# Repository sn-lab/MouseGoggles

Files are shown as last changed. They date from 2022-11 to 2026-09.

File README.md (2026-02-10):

**MouseGoggles**: A dual-SPI-display mouse-sized VR headset for mouse neuroscience and behavior research, powered by Raspberry Pi and the Godot game engine. Check out the paper at Nature Methods! https://www.nature.com/articles/s41592-024-02540-y

(left) A Raspberry Pi 4 uniquely controlling 2 circular displays. (right) Render of a head-fixed mouse on a treadmill with a VR headset

- Find a bug, have a suggestion, or want to make a feature request? Submit an [issue](https://github.com/sn-lab/MouseGoggles/issues) or start a [discussion](https://github.com/sn-lab/MouseGoggles/discussions)!

**Work in progess**

* Updating and improving [MouseGoggles EyeTrack 2.0](https://github.com/sn-lab/MouseGoggles/tree/main/Versions/EyeTrack/2.0) eye imaging quality and software improvements.

**Previous Updates**

* (Jan 2026) Added intial files for [MouseGoggles EyeTrack 2.0](https://github.com/sn-lab/MouseGoggles/tree/main/Versions/EyeTrack/2.0)! The design is now built around a single Raspberry Pi 5, aiming toward improving eye-tracking quality and a simpler assembly process (though eye-imaging quality is still being worked on).
  
* (May 2025) Big software updates to EyeTrack 1.1, including the first Godot project (2.1) which enables controlling and viewing the eye-tracking cameras from within the game engine! TCP/UDP communication between the Pis enable TTL outputs and eye-tracking videos to be controlled directly from VR experiment scripts.

* (Mar 2024) Added the [MouseGoggles EyeTrack](https://github.com/sn-lab/MouseGoggles/tree/main/Versions/EyeTrack/1.0) headset, for binocular eye/pupil tracking cameras integrated into the headset

# Building a MouseGoggles System

All versions of MouseGoggles were designed using as many readily available, off-the-shelf parts as possible, with only a minimal number of custom parts required to make assembly as simple as possible. To build a MouseGoggles system, navigate to the folder of the version you'd like to build in the [Versions](https://github.com/sn-lab/MouseGoggles/tree/main/Versions) folder and follow the included README for a comprehensive parts list, assembly guide, and software installation instructions. Since some parts included in earlier versions of the system have since been discontinued by the manufacturers, [Eyetrack version 2.0](https://github.com/sn-lab/MouseGoggles/tree/main/Versions/EyeTrack/2.0) is what we recommend building for all use-cases. Version 2.0 is built on an entirely new display platform (Raspberry Pi 5; mipi-dbi-spi) that future versions will be developed from. 

# About MouseGoggles

### The Raspberry Pi and Godot game engine

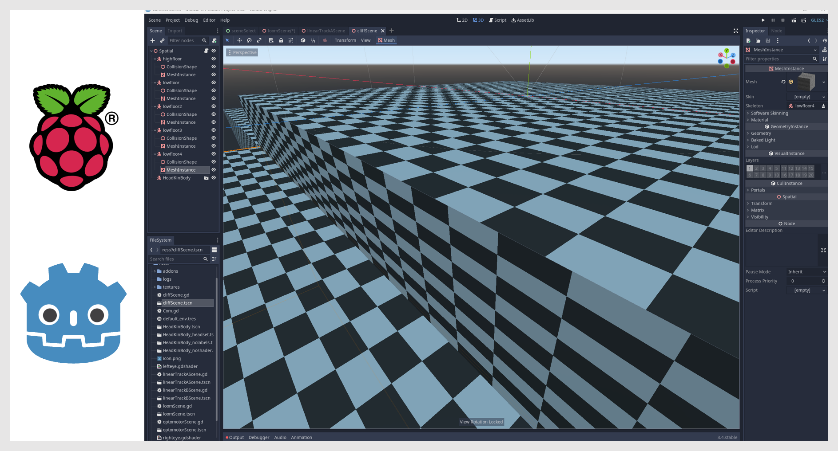
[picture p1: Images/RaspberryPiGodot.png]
Godot game engine running on a Raspberry Pi 4


The heart of the MouseGoggles system is a [Raspberry Pi 4](https://www.raspberrypi.com/products/raspberry-pi-4-model-b/) running the [Godot](https://godotengine.org/) video game engine. Since the displays are relatively low resolution (240x240), an inexpensive single-board computer like a Raspberry Pi 4 is all that's needed to effectively render visual scenes at high (>=60 fps) framerates. The multiplatform game engine Godot makes it easy to create virtual scenes and develop experimental protocols. Examples included in this repo are experiments for visual cliff avoidance, reactions to looming stimuli of various size/velocity ratios, and the syndirectional rotational optomotor response to gratings of various spatial wavelengths. The views rendered for each display are controlled by separate in-game cameras which can be tied together to match the inter-eye distance and angle of a typical mouse. Custom display shaders warp the view from each camera to match the spherical distortion of the Fresnel lenses, intended to create a realistic and immersive experience for the mouse.

### The display driver

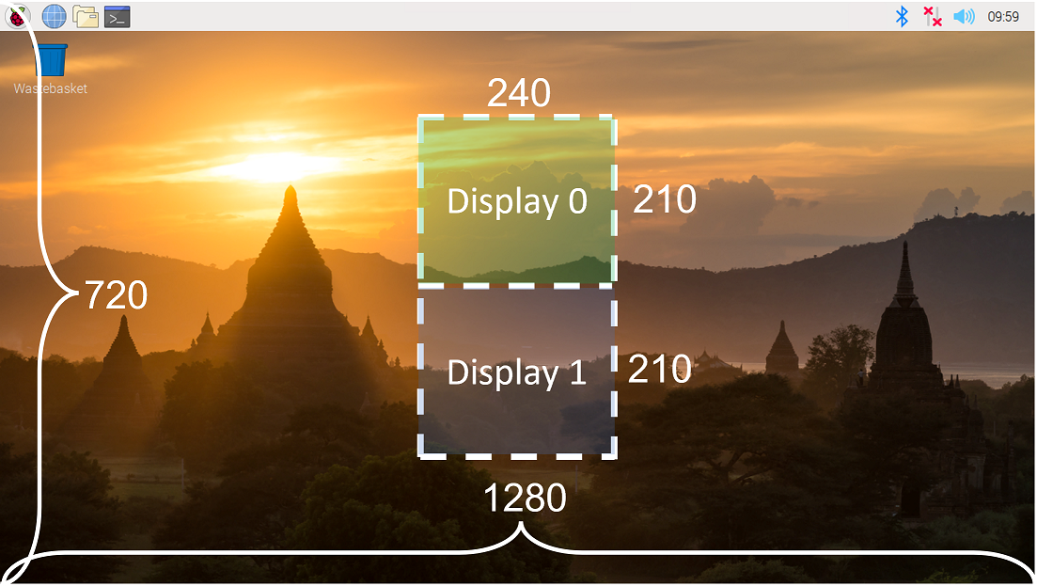
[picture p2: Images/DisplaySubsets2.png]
dual-SPI-display driver streams different frame subsets to two displays


Based on a ["blazing fast" display driver](https://github.com/juj/fbcp-ili9341) for SPI-based displays, the driver included in this repository works by copying the HDMI framebuffer and streaming the image data to the connected displays connected on the Raspberry Pi's SPI port. This means that the headset displays are not limited to displaying what is rendered by Godot; in fact, whatever is displayed on the central 240x420 (WxH) pixel region of the screen is going to be streamed to the displays. If you want to create images or video with some other program, you just have to position it in the center of the display for it to be sent to the displays -- the top 240x210 sent to display 0 (on SPI0 chip-select 0) and the bottom 240x210 to display 1 (on SPI0 chip-select 1).

### The MouseGoggles 1.0 headset

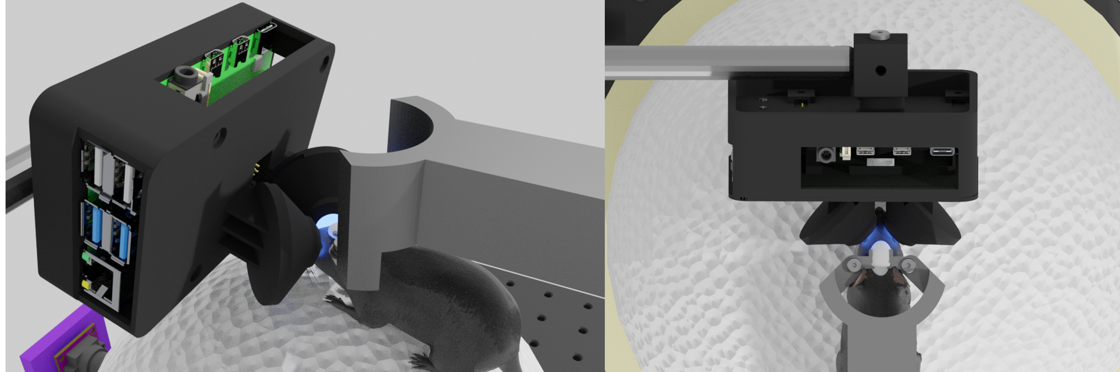
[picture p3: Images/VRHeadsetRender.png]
Render of a fully assembled MouseGoggles headset positioned for a head-fixed mouse


To create an immersive, wide field-of-view (FOV) VR headset from the dual-display Raspberry Pi, a 3D-printed headset case angles the displays inwards and sets them behind Fresnel lenses. These lenses serve two functions: to allow the displays to be positioned very close (<15 mm) to the mouse's eyes while still maintaining a comfortable infinity focal distance, and to spherically distort the displays to cover a wide FOV around each eye. Viewing angles from 0-70 degrees (0-52.5 degrees on the chipped side of the circular display) are linearly mapped onto the 240x210 circular display, resulting in an angular resolution of ~0.64 deg/pixel. With the 2 displays angled 45 degrees inward from straight ahead, the binocular headset covers a wide FOV: 140 degrees vertical and 230 degrees horizontal, with ~25 degrees of binocular overlap. Even greater horizontal FOVs are possible with greater display angles. This headset is the first official version of MouseGoggles (1.0), but newer versions have been developed which add new functionality, such as a smaller form-factor headset detached from the Raspberry Pi (1.1-1.2, 1.5), adjustable inter-eye distance (1.2-1.5), and an easier to assemble design (1.5). For more details on each MouseGoggles version, see the [Versions](https://github.com/sn-lab/MouseGoggles/tree/main/Versions) folder.

### MouseGoggles Mono 1.0

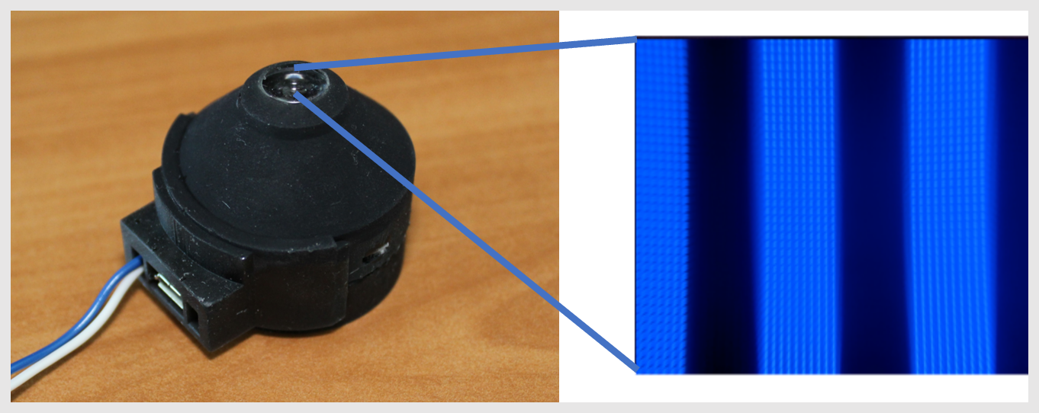
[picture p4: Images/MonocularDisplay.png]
Monocular display for basic visual stimuli (e.g. drifting gratings)


In addition to the binocular MouseGoggles system, a monocular eyepiece version can be built using a single display, lens, and microcontroller. Where the headset is ideal for complex virtual reality experiments and behavioral research, the monocular display is ideal for simple visual stimulation for basic visual neuroscience applications. The fast microcontroller [Teensy4.0](https://www.pjrc.com/store/teensy40.html) and [Adafruit graphics library](https://learn.adafruit.com/adafruit-gfx-graphics-library/overview) is used to display simple shapes and moving patterns such as drifting gratings and flickers. For more details, see [Versions/Mono/1.0]().

### Treadmills

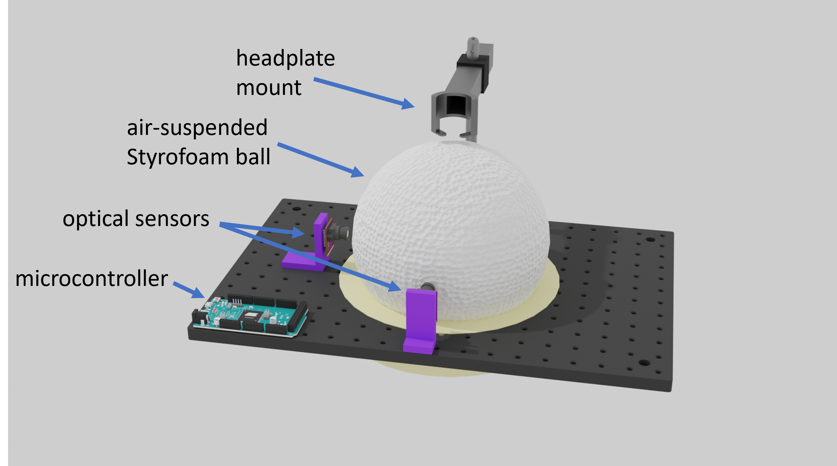
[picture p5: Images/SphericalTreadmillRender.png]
Render of a spherical treadmill system with a head mount, air-suspended Styrofoam ball, motion sensors, and microcontroller


The MouseGoggles VR headset was developed and tested using a two different treadmills for simulated walking: the spherical treadmill setup as described [here](https://pubmed.ncbi.nlm.nih.gov/19829374/) and the linear treadmill described [here](https://github.com/janelia-experimental-technology/Rodent-Belt-Treadmill/tree/main). These treadmills use sensors to detect treadmill motion and a microcontroller to transmit this movement information to external devices. By modifying the microcontroller code, we can adapt these systems to send treadmill motion to the Raspberry Pi over USB through computer mouse emulation. Forward movement (i.e. "pitch" of the spherical treadmill, or any movement of the linear treadmill) is mapped as mouse y movement, turning (i.e. "yaw" of the spherical treadmill) is mapped as x movement, and sideways motion (i.e. "roll" of the spherical treadmill) is mapped as mouse scroll wheel movement. The Godot game engine converts these detected mouse movement events into the corresponding camera movements in the virtual scene. This setup allows the human user to test the game environments and experiments using a standard computer mouse or touchpad, and to use this VR system with any type of treadmill control system that can be translated through the standard USB mouse communication protocol. To set up one of these treadmill systems with MouseGoggles (including adding a headbar and mount to head-fix a mouse above the treadmill), see the [README](https://github.com/sn-lab/MouseGoggles/blob/main/Other%20Hardware/Installation%20README.md) in the [Other Hardware](https://github.com/sn-lab/MouseGoggles/tree/main/Other%20Hardware) folder.

# Published Data

Multiple datasets have been collected for validating and testing different aspects of the MouseGoggles system for neuroscience applications, including 2-photon imaging for visual stimulation, hippocampal electrophysiology for place cell activity during virtual navigation, and video recordings of mouse behaviors during looming stimulus presentation. Check out our [preprint on Research Square](https://doi.org/10.21203/rs.3.rs-3301474/v1) for explanation and visualization of these datasets. Data, metadata, and code to process and analyze these datasets are included in the [Published Data](https://github.com/sn-lab/MouseGoggles/tree/main/Published%20Data) folder of this repository; large raw data files unsuitable for github are hosted on [Figshare](https://figshare.com/articles/dataset/Raw_image_files/24039021). 
To reproduce the published results from each of these datasets, follow the instructions in the [Description of Contents](https://github.com/sn-lab/MouseGoggles/blob/main/Published%20Data/Description%20of%20Contents.md) file, noting the software dependencies listed here:

```
* Matlab 2022b
* Python 2.8.8
* suite2p (suite2p.org)
* https://github.com/misaacson01/NoRMCorre
* https://github.com/lolaBerkowitz/SNLab_ephys
* https://github.com/nelpy/nelpy
* https://github.com/ryanharvey1/neuro_py
* https://github.com/ryanharvey1/ripple_heterogeneity
```

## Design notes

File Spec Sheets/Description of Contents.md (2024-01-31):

# Description of Contents

This folder contains specification sheets for the circular displays used in the various MouseGoggles versions. For spec sheets on the assembled display and display drivers for MouseGoggles versions 1.0-1.3, consult the files for the "1.08inch display". To more quikly refer to the pinouts of these circular displays and their connectors on MouseGoggles pcbs, refer to the pinouts.ppt file. For spec sheets relevant to the display used MouseGoggles version 1.5, consult the files for "waveshare display".

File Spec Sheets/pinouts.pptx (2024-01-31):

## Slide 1

Raspberry Pi pinouts used (for MouseGoggles)

2 | 4 | 6 GND | 8 | 10 | 12 | 14 | 16 | 18 | 20 | 22 | 24 CE0 | 26 CE1 | 28 | 30 | 32 | 34 | 36 | 38 | 40
1 3V | 3 | 5 | 7 | 9 GND | 11 | 13 | 15 reset | 17 | 19 MOSI | 21 MISO | 23 SCLK | 25 GND | 27 | 29 fmark | 31 dc | 33 | 35 | 37 | 39

Teensy 4.0 pinouts used (for MouseGoggles Mono)

| | | | | | | | | | | | reset | SCLK

GND
3V

| | | | | | fmrk | DC | | | | CE0 | MOSI

13-pin FPC connector pinouts (for 1.08” displays)

1 3V | 15 reset | 23 SCLK | 19 MOSI | 25 GND | 25 GND

25 GND | 1 3V | 24 CE0 | 31 dc | 29 FMARK | 1 3V | 25 GND

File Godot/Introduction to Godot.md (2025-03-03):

# About Godot

Godot is a free, open-source, 2D and 3D game engine popular with indie game developers, though in the context of the MouseGoggles VR system, it is a flexible experiment design platform that is powerful enough to generate complex 3D environments, yet lightweight enough to run on a Raspberry Pi 4. It can be used to generate simple 2D images, video, and animations for visual neuroscience applications, or more commonly, it can generate 3D virtual environments and conduct complex behavioral neuroscience experiments. 

Godot is multi-platform engine, meaning it can run on a PC, mac, or Linux computer. And a Godot project does not need to be compiled; this means that if you want to create or edit a Godot project on one computer, you can simply copy the project folder and run it on any other computer (even one using a different operating system) without re-compiling it there.

The [official online documentation](https://docs.godotengine.org/en/3.0/) makes it [relatively] easy to get started from scratch, and there are many excellent [tutorials](https://docs.godotengine.org/en/stable/community/tutorials.html) to help you get started. This short guide is not meant to completely replace those tutorials or make you a Godot expert, but to familiarize you with the Godot engine to the point that you're able to run VR experiments with MouseGoggles and to make simple edits and customizations of the experiments for your own purposes.

### Installing and running the Godot game engine

On a Windows or Mac PC, download the Godot Engine from [godotengine.org](godotengine.org). To use the same software version that is used on the Raspberry Pi 4, download [version 3.2](https://godotengine.org/download/archive/3.2-stable/).  

On a Raspberry Pi 4, Godot can be installed by opening the command terminal and entering each line, one at a time:

```
sudo apt update
sudo apt install flatpak
flatpak remote-add --if-not-exists flathub https://flathub.org/repo/flathub.flatpakrepo
flatpak install flathub org.godotengine.Godot
```

After installation is complete, Godot can be run on a Raspberry Pi with the following command line:

```
flatpak run org.godotengine.Godot
```

### Project manager: importing and running projects

In the context of the MouseGoggles VR system, a project can be thought of as a collection of experiments the can be edited and run on the Raspberry Pi. When Godot is first run, a project manager window will open and list all Godot projects available on your computer. If you've downloaded a project folder from elsewhere (e.g. from a Github repository, or from another computer), this project will need to be imported by Godot before it can be edited or run. 

To import a project, start the Godot program to be brought to Godot's project manager. Click the `import` button on the right, and navigate into your new project folder. Locate the `project.godot` file inside that folder and select it to import the project. After being imported, the project can be run directly, or it can be opened into the Godot Editor where all of the project's experiment files can be read and modified. The project can also be run from inside the editor by clicking the small green arrow on the top-right side of the window.

### Editor

In the Godot Editor window, there are mutliple menus and panels that give you access to view and edit different aspects of the project. Across the top are the main menus where overall project settings and defaults can be customized (e.g. Scene, Project, Debug, and Editor), followed by the workspace tabs where different project files can be viewed and modified (e.g. 2D scene, 3D scene, and script files). Along the left and right sides of the window are the panels (e.g. Scene, Filesystem, and Inspector) which offer more granular views of specific files, scenes, and nodes in the project. And in the center of the window is the main workspace, where the currently selected file (scene or script) can be visualized. 

##### Scenes, Nodes, and Scripts

Building a game or experiment with the Godot editor is primarily accomplished using scene and script files. The "scene" file (denoted by the `.tscn` file extension) defines the contents and layout of a virtual environment, and the script file (denoted by the `.gd` file extension) contains instructions for how the scene functions, or how a user (human or mouse) interacts with the scene. 

A scene is built from a series of nodes, which can be thought of as environmental building blocks that give new characteristics to the scene. Nodes are hierarchical: they can be "children" of the scene, where new objects or surfaces (for example) can be defined, or they can be children of other nodes, giving additional characteristics (e.g material or physical properties) to its parent node. In MouseGoggles Godot projects, nodes are often used to build objects or surfaces in the 3D scene; for example, the `MeshInstance` node can create a surfaces for the objects, floors, or walls of a 3D environment.

After the 3D layout has been defined by a scene file, a script file (or files) can be attached to the scene to control the behavior of the scene and define events that take place in that scene. Godot scripts use the object-oriented programming paradigm, not unlike C++ or Python, so some programming knowledge is required to perform significant edits to the experiment or to create new experiments (Godot recommends this free, online Intro to Computer Science course [CS50x 2024](https://cs50.harvard.edu/x/2024/) as a general programming tutorial). Scripts can be attached to any node of a scene, where the script will control the behavior of that node. In MouseGoggles Godot projects, scripts are typically attached to the root (i.e. parent)`spatial` node of a 3D scene, which then defines the logical flow of an experiment using that scene. Script files tend to be structured with a familiar programming layout, beginning with defined variables at the top, followed by a setup function that runs once at the beginning of the experiment (`func _ready():`), a loop function that runs for every rendered frame of the experiment (`func _process(delta):`), and finished with any additional functions that may be called by the script. Properties of a scene (e.g., the [x,y,z] location of a virtual object located the scene) can be assigned to variables at the top of the script and then modified during the script's functions, thereby granting the script the power to control the properties of the scene and define an experiment.

### Experiment log files

The example Godot experiments for MouseGoggles use a common format for logging experimental data. This format consists of logging the state of a number of variables for every frame. That is, each time the game loop executes, the state of those variables is logged. At the end of each experimental trial, a section of this code will save these variables in a .csv file, in the `logs` folder inside the Godot project folder. 

Each column of data in the csv file represents the values of a single variable; the header at the top of the file shows the descriptive name of these variables. Each row of the csv file shows the value of these variables for each frame.

Different experiments are designed to store different variables that are important for that experiment. For example, in experiments featuring 2D navigation, the mouse's position (x,z) and it's current orientation are important to log, whereas in experiments with only 1D navigation, only the mouse's z position needs to be logged.

### Calibrating an existing experiment

At the top of each experiment script (e.g. `linearTrackScene.gd` in Godot project 1.6), variables are set which descibe many of the experiment's parameters. Some of these parameters may need to be changed depending on your specific experimental setup. Beginning in Godot project 2.0, many of these parameters which are common across all experiments (e.g. parameters about the headset configuration) are instead contained in the `commonSettings.gd` script to remove redundancy. Listed below is a few parameters which are mostly likely to change, though for each experiment you run, it is wise to first look through all of the parameters to verify they make sense for your experiment.

* `trial_duration`: The duration (in s) of each trial, before a timeout is reached and the next trial starts.

* `num_reps`: The number of trial repetitions before the experiment is finished.

* `eye_pitch`: The pitch angle (in degrees) of the headset, relative to the horizon.

* `head_roll`: The roll angle (in degrees) of the headset, relative to the horizon.

* `mouse_gain`: The movement sensitivity of input signals: higher values will increase the speed virtual movement.

### Creating a new experiment

If you want to design new experiments of your own, you may choose to follow the tutorials listed at the top to create a new exxperiment from scratch. Alternatively, a simpler, faster way to create an experiment is to select an existing experiment that most closely matches the experiment you'd like to create, and copy/customize that experiment. The following instructions provide general guidance on creating a new experiment this way by copying and editing an existing project.

1. Copy the existing project, and give it a new name
   
   * Copy the "MouseVR Godot Project X.X" folder that you wish to adapt, and give the copy a unique name
   
   * Open Godot, and in the project manager window, import the new project folder you just created. The project will still have the original project name, so rename it to match the new folder you just created (In the editor window: Project>Project Settings>Config>Name)

2. Run the new project, copy an existing experiment, and give it a new name
   
   * From the project manager, edit the new project you just created
   
   * Selecting the experiment you wish to modify, copy both the .tscn and .gd files of that experiment. Rename these copied files to describe your new experiment.
     
     (e.g. `new_exp.tscn`; `new_exp.gd`)
   
   * Open up the .tscn file of your new experiment, and view it in the `3D` tab. In the Scene tab, identify the `spatial` node that has an attached script. This will still be the original script that you copied from, so right click the node to detach this script. Right click the node again to attach the new script you just created.

3. Edit the new experiment
   
   * Open the new .tscn file you created and view it in the `3D` tab. Edit the nodes and properties to adapt the scene to fit your desired experiment
   
   * Open the new .gd script you created and view it in the `script` tab. Modify the code to fit your desired experiment.

4. Add the new experiment to the "scene select"
   
   * Open up the sceneSelect.tscn file, and view it in the `2D` tab
   
   * In the Scene window, copy the last MarginContainer node (e.g. "MarginContainer9") and paste it in the empty space below. This will create a new margincontainer and child button node. Rename the MarginContainer node (e.g. "MarginContainer10") and drag it so that it is a child of the VBoxContainer node. This will move your new button to the top of the list of scene buttons. Since this new button will still have the same name as the button you copied, click on the new button, and in the Inspector window, rename the text to match your new experiment.
   
   * Open up the sceneSelect.gd file and view it in the `script` tab.
   
   * Copy a scene variable and rename it to match your new MarginContainer# and new experiment name 
     
     (e.g. `onready var  new_exp_button = get_node("HBoxContainer/VBoxContainer/MarginContainer10/Button")`)
   
   * in the `_ready():` function, copy a line and rename it to match your new scene variable and create a new experiment callback function.
     
     (e.g. `new_exp_button.connect("pressed",self,"_load_new_exp")`)
   
   * Copy a callback function and rename it to the function name you just created, and set it to load your new experiment.
   
   * (e.g. `func _load_new_exp():
     
         get_tree().change_scene("res://new_exp.tscn")`)

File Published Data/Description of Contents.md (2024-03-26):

# Description of Contents

This folder contains datasets and code used in the intial MouseGoggles publication. Raw data, pre-processed data, and analyzed data is included in the "data" folder when possible; large raw data files unsuitable for github are hosted by [FigShare](https://figshare.com/articles/dataset/Raw_image_files/24039021).
For each dataset, Matlab and/or python code used to process and plot data are included. The sections below detail the contents of each dataset folder and how the publication data can be reproduced.

### 2P Imaging

This folder contains two-photon imaging data, experimental protocol metadata, and processing/plotting code for 3 mouse imaging sessions. Raw Imaging data files too large for github are hosted by Figshare at the link above. Also on Figshare are the motion corrected calcium imaging data files associated with these raw data files, located here: https://figshare.com/account/items/24039042
To reproduce the published results from preprocessed data files included in this folder, open the `monoDisplay_VR2_analysis.m` file in Matlab and run section 3. 
Alternatively, To reproduce the data from raw imaging files, download the files from figshare and put each of the 3 raw imaging files into the associated mouse folder (e.g., "rfm0d0t0_mouse1.tif" into the "mouse1" folder). Next open the `monoDisplay_VR2_analysis.m` file in Matlab and run sections 1 and 2 for each mouse folder individually to preprocess these raw imaging files. Section 1 extracts the TTL synchronization signal from the imaging data (indices of the imaging frames at the start of every experimental stimulus set will be contained in the `starts.mat` file) and creates motion-corrected calcium image files. Following the instructions in section 2, these calcium imaging files must next be loaded into suite2p for automatic ROI segmentation and neuron activity extraction, which will generate a "suite2p" folder of data for each imaging file. All neuron activity data needed for analysis and plotting will be contained in`>suite2p>plane0>Fall.mat`. After this has been performed for each mouse dataset, section 3 of `monoDisplay_VR2_analysis.m` can be run to analyze and plot the data. Note however the example neuron plots in section 3 may not work well if the suite2p dataset has changed; if that is the case, new example neurons should be found through manual inspection of the data.
For more details about experimental protocol or to reproduce the experiment yourself, `monoDisplay_VR2_presentation.m` is the monocular display control script which generated and presented the stimulus sets used in this dataset.

### Looming

This folder contains behavioral scoring details and data from 2 independent semi-blind scorers to find mouse startle reactions to looming visual stimuli. In the "Reaction Log" .xlsx files, scorers were given instructions as to how to score video clips of mice reacting to looming stimuli from either a projector VR system or the MouseGoggles VR system. These video clips are stored on Figshare at the link above, in the "loom_videos.zip" file. To reproduce the published results from this dataset, run the `analyze_manual_loom.m` script in Matlab.

### Linear track

This folder contains all logged data from the 5-day continuous loop linear track place learning protocol, performed with 10 mice over 2 datasets. Each dataset contains logged data for 40 track traversals each day over 5 days, from 5 mice. Due to some occasional Raspberry Pi/Godot glitches, some experiments had to be restarted resulting in >40 traversals for some mice on some days; these extra traversals are unused in this analysis. In all logged data files, data is stored in csv format, where each line stored data for a single frame of the game loop, and the columns each store a unique datatype according to the following structure:
column 1: spherical treadmill yaw motion
column 2: spherical treadmill pitch motion
column 3: spherical treadmill roll motion
column 4: mouse x (horizontal) position (locked at 0.5 in this experiment)
column 5: mouse z (position along track) position
column 6: mouse head angle (locked at 180 degrees in this experiment)
column 7: water reward given signal
column 8: lick sensor detection signal
column 9: timestamp (in ms, from program start)
To reproduce the published results from this data, run the `analyze_godot_lineartrackV5B_allsets.m` script in Matlab. To reproduce or visualize this experiment, open the Godot program and select the 'linear track' scene, defined by the game program file `linearTrackScene.gd` in the Godot project folder.

### CA1 Ephys

This folder contains code for processing and plotting electrophysiological recording during continuous loop linear track traversal. The data used by this code is stored according to [CellExplorer data format standards](https://cellexplorer.org/datastructure/data-structure-and-format/) and hosted by Figshare at the link above.
To reproduce the published results from this dataset, download the VR_ephys_8sessions.zip file and unzip it into the CA1 Ephys folder. To plot the processed data, the `plot_vr_place_cells.ipynb` notebook calls the main processing script located in `vr_place_cells.py`. For Windows 10 users, the full environment to run this notebook/script can be installed by creating a conda environment using the environment.yml.

### Eye Tracking

This folder contains code and data for processing and plotting eye/pupil tracking during looming visual stimuli presented to head-fixed mice walking on a linear treadmill. Most raw and processed data are located in this folder, while larger eye tracking and gameplay videos are hosted by Figshare at the link above.

To only reproduce data plots from processed tabular data, this folder contains all the necessary data and code. To fully reproduce the results from this dataset from raw videos, the "MouseGoggles EyeTrack Videos" .zip file will needed to be downloaded from figshare and copied into their matching folders in this repository. 

To reproduce the eye tracking camera calibration, run the `camera_calibration.m` Matlab script loacted in the Camera calibration folder. To preprocess and extract eye data from deeplabcut-labelled eye tracking videos and logged data files, run the `Preprocess_EyeTrack_Loom.m` Matlab script. To generate plots from preprocessed tabular data files, run the raw `Analyze_EyeTrack_Loom.m` script.

### software dependencies

    * Matlab 2022b
    * Python 2.8.8
    * suite2p (suite2p.org)
    * https://github.com/misaacson01/NoRMCorre
    * https://github.com/lolaBerkowitz/SNLab_ephys
    * https://github.com/nelpy/nelpy
    * https://github.com/ryanharvey1/neuro_py
    * https://github.com/ryanharvey1/ripple_heterogeneity

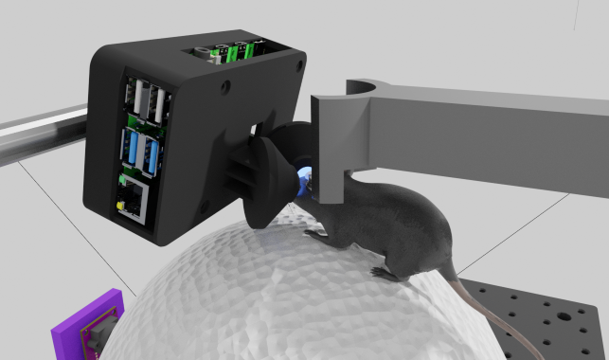
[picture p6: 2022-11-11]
Images/VRwithBallRender.png

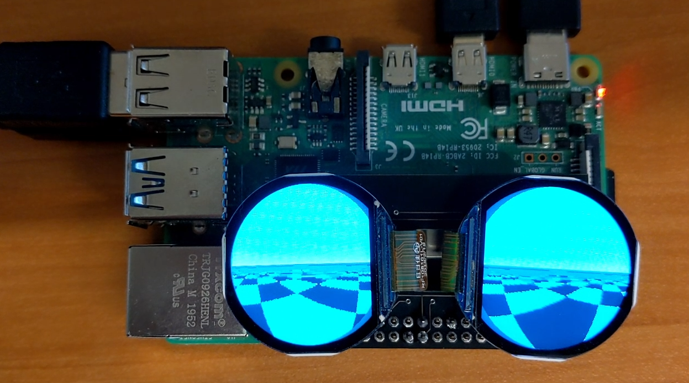
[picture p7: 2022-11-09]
Images/RaspberryPi2Displays.png

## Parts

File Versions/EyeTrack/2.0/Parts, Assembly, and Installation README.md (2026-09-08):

(left) 3D render of assembled MouseGoggles EyeTrack 2.0. (right) Picture of assembled MouseGoggles EyeTrack 2.0

# 

**NOTE:** This version is currently in development and is subject to change; if you proceed with building this version and notice any mistakes or problems, please raise an [issue](https://github.com/sn-lab/MouseGoggles/issues/new) on Github!

Recent changes:

- Changed parts list for a more IR-sensitive camera from Arducam (6/8/26)

- Added a software installation section on calibrating the cameras (6/8/26)

# Parts List

---

### Off-the-shelf parts

The table below lists all off-the-shelf parts required to build MouseGoggles EyeTrack 2.0, a re-design of the EyeTrack headset built entirely around a single Raspberry Pi 5! This version features newer parts and a simpler assembly and installation process. 

Follow the links below to purchase the parts in the quantities listed (though you may consider ordering spare parts as well). If any parts are out of stock at the links below, other suppliers are often available (e.g. Digikey stocks many Adafruit parts). In addition to these listed parts, you will also need some basic computer peripherals (HDMI monitor, USB keyboard and mouse /touchpad, microSD card reader), at least for the initial setup.

* Note: if you intend on frequently acquiring eye-tracking videos, consider purchasing a MicroSD card with more storage space (e.g. 512 GB)

| Part Name                                       | Description                                           | Link                                                                                                  | Est. Unit Cost (USD) | Quantity |
| ----------------------------------------------- | ----------------------------------------------------- | ----------------------------------------------------------------------------------------------------- |:--------------------:|:--------:|
| Raspberry Pi 5 - 4GB                            | Raspberry Pi 5 Single-board computer                  | [PiShop.US](https://www.pishop.us/product/raspberry-pi-5-4gb/)                                        | $85                  | 1        |
| Class 10 - MicroSD Card Extreme Pro - 32 GB     | MicroSD card to Raspberry Pi OS                       | [PiShop.US](https://www.pishop.us/product/class-10-microsd-card-extreme-pro-32-gb-blank-bulk/)        | $23                  | 1        |
| Micro-HDMI to HDMI cable for Pi 4 - 3ft, Black  | HDMI adapter to connect Raspberry Pi to monitor       | [PiShop.US](https://www.pishop.us/product/micro-hdmi-to-hdmi-cable-for-pi-4-3ft-black/)               | $6                   | 1        |
| FM01 1" Near-IR Hot mirror                      | Hot mirror for eye tracking camera                    | [Thorlabs](https://www.thorlabs.com/thorProduct.cfm?partNumber=FM01)                                  | $42                  | 1+spare  |
| FRP0510 1/2" Fresnel Lens - f = 10 mm           | Fresnel lens for VR headset                           | [Thorlabs](https://www.thorlabs.com/thorproduct.cfm?partnumber=FRP0510)                               | $22                  | 2        |
| NoIR Spy camera for Raspberry Pi                | Infrared-sensitive mini cameras for eye/pupil imaging | [Arducam](https://www.arducam.com/1-4-5-noir-mpspy-camera-module-sensor-flex-cable-raspberry-pi.html) | $30                  | 2        |
| Female/Female Jumper Wires                      | 20x12" Jumper wires                                   | [Adafruit](https://www.adafruit.com/product/1949)                                                     | $4                   | 1        |
| Raspberry Pi 5 Power Supply                     | USB-C power supply                                    | [Adafruit](https://www.adafruit.com/product/5814)                                                     | $14                  | 1        |
| FPC Camera Cable - 22-pin to 15-pin, 200mm long | Cable to connect camera modules                       | [Adafruit](https://www.adafruit.com/product/5818)                                                     | $3                   | 2        |
| CSI or DSI Cable Extender                       | 15 pin cable extender                                 | [Adafruit](https://www.adafruit.com/product/3671)                                                     | $3                   | 2        |
| 1.28" 240x240 Round TFT LCD                     | Display for VR headset                                | [Adafruit](https://www.adafruit.com/product/6178)                                                     | $18                  | 2        |
| Super-bright 5mm IR LED                         | IR LED for pupil illumination                         | [Adafruit](https://www.adafruit.com/product/387)                                                      | $1                   | 2+spares |
| 100 Ohm through-hole resistors - pack of 25     | Resistors for LED circuit                             | [Adafruit](https://www.adafruit.com/product/4293)                                                     | $1                   | 1        |
| 2-56 thread, 1/2" length socket head screws     | Pack of 1/2" long screws to assemble parts            | [McMaster](https://www.mcmaster.com/91251A081/)                                                       | $10                  | 1        |
| 2-56 thread, 3/16" wide narrow hex nuts         | Pack of hex nuts to assemble parts                    | [McMaster](https://www.mcmaster.com/90730A003/)                                                       | $4                   | 1        |
| **Total (est.)**                                |                                                       |                                                                                                       | $343                 |          |

### Recommended tools

| Part Name         | Description                                                 | Link                                                                                    | Est. Unit Cost (USD) |
| ----------------- | ----------------------------------------------------------- | --------------------------------------------------------------------------------------- | -------------------- |
| Needle file       | File for sanding/smoothing 3D prints                        | [McMaster](https://www.mcmaster.com/4261a37/)                                           | $19                  |
| Hex wrench        | Wrench for assembling headset                               | [McMaster](https://www.mcmaster.com/7122A15/)                                           | $1                   |
| Glass scribe      | Simple glass scribe for cutting hot mirror to size          | [Grainger](https://www.grainger.com/product/GENERAL-TOOLS-Scriber-Straight-3ZZP6)       | $12                  |
| Silicone adhesive | Electronics grade adhesive for extra support of parts/wires | [Digikey](https://www.digikey.com/en/products/detail/chip-quik-inc/EGS10C-20G/10059587) | $5                   |
| Soldering iron    | Soldering iron for attaching jumper wires to displays       | [Adafruit](https://www.adafruit.com/product/4921)                                       | $60                  |
| Soldering wire    | for soldering jumper wires                                  | [Adafruit](https://www.adafruit.com/product/1930)                                       | $18                  |
| Wire strippers    | for stripping jumper wires                                  | [Adafruit](https://www.adafruit.com/product/527)                                        | $18                  |
| Flush cutters     | for trimming ends of soldered wire                          | [Adafruit](https://www.adafruit.com/product/152)                                        | $7                   |

### 3D prints

The table below lists all custom 3D-printable parts required for this version of MouseGoggles. Follow the links below for .stl files to print these parts on your own 3D printer or to send to a 3D printing service such as [CraftCloud](https://craftcloud3d.com/). 

For most parts, a z-resolution of <=0.1 mm is recommended, while for the "Bracket" and "Mount" parts, greater material strength is preferred and <=0.3 mm z-resolution is adequate.

For strong, long-lasting parts, an FDM-based printer using PLA is a good choice, such as the [Original Prusa MK4S](https://www.prusa3d.com/product/original-prusa-mk4s-3d-printer-5/) or the [Elegoo Neptune 4](https://us.elegoo.com/collections/fdm-printers/products/elegoo-neptune-4-fdm-3d-printer). For higher resolution parts, UV-cured resin-based SLA printers such as the [Photon Mono M7](https://store.anycubic.com/products/photon-mono-m7) can also produce adequate and cost-effective parts, though resin-based prints can become brittle over time and are often semi-transparent. To reduce stray light from semi-transparent headset prints, parts can be painted with an opaque paint (e.g. [Black 3.0](https://www.culturehustleusa.com/products/black-3-0-the-worlds-blackest-black-acrylic-paint-150ml)).

| Part Name                | Description                           | Link                                                                                                                  | Quantity | Aprox. Dimensions (mm) |
| ------------------------ | ------------------------------------- | --------------------------------------------------------------------------------------------------------------------- | -------- | ---------------------- |
| Eyepiece V2.stl          | Main eyepiece enclosure               | [stl](https://github.com/sn-lab/MouseGoggles/blob/main/Versions/EyeTrack/2.0/3D%20Prints/Eyepiece%202.0%20V1.stl)     | 2        | 41x36x12.5             |
| LensClip V1.stl          | Clip for securing Fresnel lens        | [stl](https://github.com/sn-lab/MouseGoggles/blob/main/Versions/EyeTrack/2.0/3D%20Prints/LensClip%20V1.stl)           | 2        | 17x12x4                |
| CameraClip V2.stl        | Clip for securing Camera and LED      | [stl](https://github.com/sn-lab/MouseGoggles/blob/main/Versions/EyeTrack/2.0/3D%20Prints/CameraClip%20V1.stl)         | 2        | 25x8x5                 |
| EyepieceBack V1          | Backing of eyepiece                   | [stl](https://github.com/sn-lab/MouseGoggles/blob/main/Versions/EyeTrack/2.0/3D%20Prints/EyepieceBack%202.0%20V1.stl) | 2        | 40x28x6                |
| Bracket50 V1.stl         | Headset frame (50 deg eyepiece angle) | [stl](https://github.com/sn-lab/MouseGoggles/blob/main/Versions/EyeTrack/2.0/3D%20Prints/Bracket50%20V1.stl)          | 1        | 79x52x43               |
| MirrorStencilBase V1.stl | Base of glass cutting stencil         | [stl](https://github.com/sn-lab/MouseGoggles/blob/main/Versions/EyeTrack/2.0/3D%20Prints/MirrorStencilBase%20V1.stl)  | 1        | 40x30x3                |
| MirrorStencil V1.stl     | Stencil for glass cutting             | [stl](https://github.com/sn-lab/MouseGoggles/blob/main/Versions/EyeTrack/2.0/3D%20Prints/MirrorStencil%20V1.stl)      | 1        | 44x34x4.5              |

# Hardware Assembly Instructions

---

### Assemble the MouseGoggles headset

Select steps of MouseGoggles EyeTrack 2.0 assembly

1. Separate a group of 7 jumper wires from the bundle. Cut the sockets off of one end of the wires and strip the cut end of the wire. Solder the 7 exposed wires into the back of a circular display to the following pins: 3Vo, Gnd, SCK, MOSI, TFTCS, RST, DC. (it is not necessary to connect Vin, MISO, SDCS, Lite). Repeat with a 2nd display.

2. Cover the soldered pins and base of the wires with silicone glue, to give extra support to the junction and prevent wires breaking when bent. (the glue may take up to 24 hours to fully cure)

3. Insert a hot mirror into the MirrorStencilBase, and set the MirrorStencil on top. Holding the mirror and stencil stable with one hand, gently scratch the mirror using the glass scribe along the 3 lines in the stencil, going over each line multiple times. After the glass has been scored, flip the MirrorStencil parts inside out and sandwich the mirror in between the two flat surfaces of the part, so that the mirror is sticking halfway out and the score line follows the straight edge of the MirrorStencil as closely as possible. Clamping the mirror between the stencil, gently press the exposed half of the mirror to snap the mirror along the central score line. Then, for each half of the mirror, expose the other sections and break along the smaller score lines to finish roughly shaping the mirror (these smaller score lines to not need to bread as cleanly since they will be largely out of the mouse's view). Slide each mirror all the way into the mirror slot of the eyepieces to check the fit - ideally it should roughly follow the shape of the eyepiece without extruding too much.
   
   * Tips: Adding a drop of liquid to the score line can help ensure that the glass snaps along the line. To chip away smaller pieces of glass, you can use the metal back end of the scribe to press and break the glass edge. This broken edge does not need to be a clean edge since it is not visible inside the eyepiece. Instead of/in addition to a glass scribe, a dremel tool with diamond grinding tip can be an easy way to shape the cut end of the glass.

4. Insert a camera into the camera port, with the ribbon cable oriented in the direction opposite of the eyepiece front. 

5. Insert an IR LED into one of the two circular LED ports next to the camera port.
   
   * Note: If any part is too difficult to slide into place, use a needle file to sand down any warped areas or imperfections of the 3D prints.

6. Slide a CameraClip part into the eyepiece, roughly securing the camera and LED in place. For extra security, add dabs of adhesive to fix the clip to the eyepiece

7. Stack the circular display on top of the eyepiece, with the display screw-holes aligned to the screw holes on the side of the eyepiece opposite of the camera port.

8. Stack the EyepieceBack onto the display/eyepiece, with all four open screw holes aligned to the four screw holes of the eyepiece, and with the camera ribbon cable sitting between the EyepieceBack and the display so that it is protected, secured, and lines up with the soldered jumper wires. From the eyepiece-side, Insert four 1/2" screws through the holes, but don't secure them with nuts yet.

9. Repeat steps 4-8 with a second eyepiece.

10. (for horizontally-mounted eyepieces) Position the two eyepieces onto the bracket so that 3 of the 4 screws of each eyepiece extend through the inner bracket slots. Then add nuts to all four screws to secure the eyepiece together and to the bracket.

11. Insert a Fresnel lens into each slot on the front of the eyepieces, with the ridged side of the lens facing into the eyepiece and the smooth side facing out of the eyepiece (very gently sliding your finger or fingernail along each flat face of the lens will tell you which side is smooth and which side is ridged). Attach a LensClip to each eyepiece to hold the lens in place. (the thicker end of the LensClip should be oriented so that it will sit above the mouse's eye, not below it.

### Wire up the displays, cameras, and LEDs

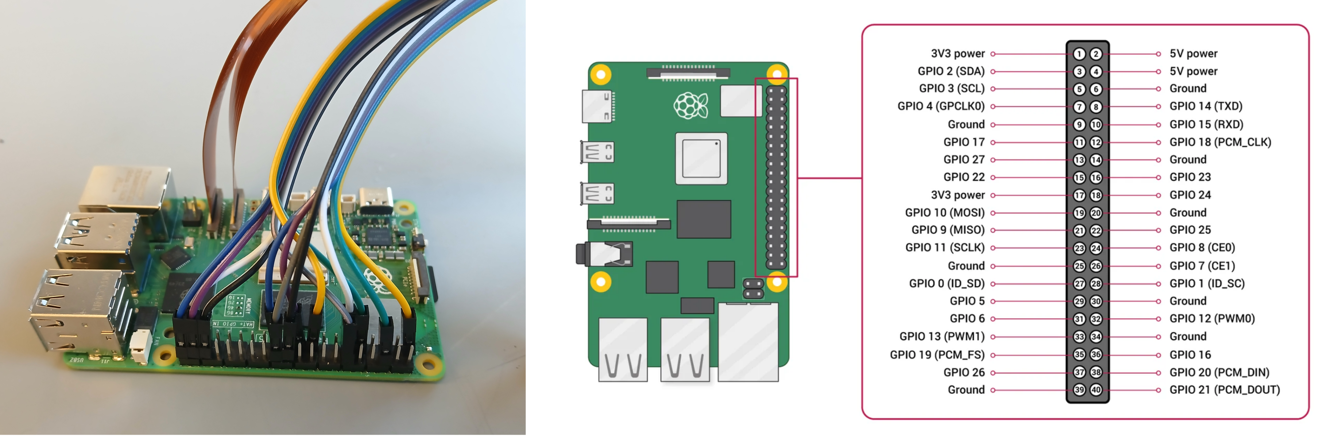
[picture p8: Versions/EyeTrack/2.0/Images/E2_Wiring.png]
(left) Wired connections of a MouseGoggles EyeTrack 2.0 to a Raspberry Pi 5. (right) Pin names and numbers of the Raspberry Pi 5 40-pin header.


1. The Raspberry Pi cameras must first be manually refocused so that imaging of the eyes and pupils (which will sit very close to the camera) are clear and sharp. This requires breaking/removing the drop of glue which fixes the camera lens in place, then rotating the lens CCW for a more close-up focus. To locate the glue, look at the center circular plastic piece which holds the camera lens - at the seam where the circular lens holder rotates (near the notches), find the shiny, hardened drop of glue on one side of it. To break it, use some small scissors or sharp flush/diagonal 
   cutters to cut through this drop of glue along the seam, and/or forceps to remove broken glue from the seam. Once the glue is broken or mostly broken, use forceps or a flush cutter to grab the notches and rotate the circular lens holder, taking care not to scratch the lens in the center. Once it starts to freely rotate, unscrew the lens (rotate CCW) by ~1.25 rotations (450 degrees) to set a better close-up focus.

2. Connect each camera ribbon cable to a CSI extender, then to the 15-pin side of a 22-15 pin ribbon cable. Connect the left eye camera to the cam/disp 0 connector of the Pi 5, and the right eye camera to cam/disp 1.

3. Connect the anode pin of each LED (the longer of the two) to it's own jumper wire, then connect a resistor to the other end of each jumper wire. Connect each resistor to a 5V pin on the Raspberry Pi 5 header, and the cathode pin of each LED (the shorter of the two) to a ground pin on the Raspberry Pi 5 header, following the map below (refer to Pi 5 pin names in the image above):
   
   | LED pin                   | Raspberry Pi 5 pin |
   | ------------------------- | ------------------ |
   | LED 1 - long pin/resistor | pin 2 (5V power)   |
   | LED 1 - short pin         | pin 14 (Ground)    |
   | LED 2 - long pin/resistor | pin 4 (5V power)   |
   | LED 2 - short pin         | pin 20 (Ground)    |

4. Connect the jumper wires of the left eye (display 1) and right eye (display 2) displays to the header pins of the Raspberry Pi 5 following the map below (refer to Pi 5 pin names in the image above):

| Display pin       | Raspberry Pi 5 pin         |
| ----------------- | -------------------------- |
| Display 1 - V+    | pin 1 (3V3 power)          |
| Display 1 - GND   | pin 6 (Ground)             |
| Display 1 - SCK   | pin 23 (GPIO 11, SCLK)     |
| Display 1 - MOSI  | pin 19 (GPIO 10, MOSI)     |
| Display 1 - TFTCS | pin 24 (GPIO 8, CE0)       |
| Display 1 - RST   | pin 11 (GPIO 17)           |
| Display 1 - DC    | pin 22 (GPIO 25)           |
| Display 2 - V+    | pin 17 (3V3 power)         |
| Display 2 - GND   | pin 9 (Ground)             |
| Display 2 - SCK   | pin 40 (GPIO 21, PCM_DOUT) |
| Display 2 - MOSI  | pin 38 (GPIO 20, PCM_DIN)  |
| Display 2 - TFTCS | pin 12 (GPIO 18, PCM_CLK)  |
| Display 2 - RST   | pin 37 (GPIO 26)           |
| Display 2 - DC    | pin 36 (GPIO 16)           |

* Note: to make the electrical wiring more secure, consider these options: Trim the length of the LED and resistor pins with wire cutters to reduce the amount of exposed wire; Cover exposed wire with electrical tape; Secure female/male connections with electrical tape or silicone adhesive; Solder wire connections together and cover with shrink tubing for the most secure connections.
* Note

# Software Installation Instructions

---

To install all necessary software, you'll first need a PC to install the Raspberry Pi OS to the MicroSD card that will be installed in the Raspberry Pi. Next, you'll need to start up the Raspberry Pi and install the necessary software (Godot game engine, display settings, camera software).

## Installing software

### Install the Raspberry Pi 5 Operating System

- Insert a blank micro SD card into your PC
- Download and install the [Raspberry Pi Imager](https://www.raspberrypi.com/software/)
- Choose Device: "Raspiberry Pi 5""
- Choose OS: "Raspberry Pi OS (64-bit)"
- Choose Storage: -select your SD card-
- When asked if you would like to apply custom OS settings, click "Edit Settings"
- Set the hostname, username, password, WiFi, and localisation settings as desired, then click save and exit the settings window (where applicable in the following instructions, the hostname will be assumed to be "MG2")
- Select "write" to install the OS with your custom settings
- After the image has finished writing, Insert the SD card into your Raspberry Pi and power it on

### Download the MouseGoggles repository

- Start the Raspberry Pi and connect to the internet.
  
  - to connect to a wireless internet network, you may first be asked to set your wireless LAN country

- Open up the Raspberry Pi command terminal and enter each line, one at a time:
  
  ```
  sudo apt-get update
  sudo apt-get upgrade
  sudo apt install python3-opencv
  cd ~
  git clone https://github.com/sn-lab/MouseGoggles
  ```

- Note: If you are asked if you want to continue installing, answer yes.

### Set up the displays

- Open up the Raspberry Pi command terminal enter each line, one at a time, to copy the display driver and to edit the Raspberry Pi configuration file: (scroll to see the full line).
  
  ```
  sudo cp ~/MouseGoggles/Versions/EyeTrack/2.0/Install/gc9a01.bin /lib/firmware/
  sudo nano /boot/firmware/config.txt
  ```

- In a separate window (leave the command terminal open), open the file located in:`MouseGoggles/Versions/EyeTrack/2.0/Install/configtxt.txt`.

- Copy the entire configtxt contents into the bottom of the config file (just below the `[all]`section).

- Restart the PC.

- When the computer reboots, right-click on the desktop and select `Desktop Preferences`.

- Scroll down the menu on the left to select the `Screens` tab.

- Drag the screens so that the SPI-1 screen is on the top-left corner and the SPI-2 screen is just to the right of SPI-1 (the screens should snap so that they are linked on their edges). If there is an HDMI screen, drag that so it is also aligned to the top-left corner, sitting underneath both SPI screens.

- If you have mounted the eyepieces on the bracket vertically (i.e. with the jumper wires extending upwards above the bracket), you can skip the next line.

- If you have mounted the eyepieces on the bracket horizontally (i.e. with the jumper wires extending towards the center of the bracket), right-click on the SPI-1 screen and set "Orientation" to "Right", then right-click on the SPI-2 screen and set "Orientation" to "Left".

- Apply and click "ok" to accept the changes.

### Calibrate the cameras

- Navigate to the "pi5cam.py" file in the MouseGoggles/Versions/EyeTrack/2.0/Python folder. Double-click this file to open and view it with a code editor (you may need to drag and resize the window to see the full editor). At the top of the script, find the "Configuration" section --this is where settings can be edited to improve the quality of eye tracking imaging. 
- Check that the "base_log_dir" variable is pointing at the correct location of your Godot logs folder (you will likely need to change "mg2" to the username you've chosen for this installation.
- Click the "run" (arrow) button at the top of the window to check the live view of the cameras. Click "q" on your keyboard to stop the cameras when you are done.
- Set the "CROP_ENABLED" variable to "True" to enable a cropped/zoomed view of the pupils. You may need to change the width, height, x, and y variables of each camera so that both eyes are centered in the cropped region. Click the run button again to check your settings. 
- Keep adjusting the configuration and checking the cameras until you are satisfied with the quality and view of the eye tracking imaging. Once the configuration is final, copy the entire "Configuration" section and paste it in the "pi5cam_udp.py script" to replace the default configuration. This UDP script is what is used by the Godot game engine to view and record the eyes during VR experiments

# Operating Instructions

---

### Starting the game engine and running experiments

- Navigate to the "pi5cam_udp.py" file in the MouseGoggles/Versions/EyeTrack/2.0/Python folder. Double-click this file to open and view it with a code editor. Click the "run" (arrow) button at the top of the window to start the camera controller. A command window will open and display messages about this controller: once you see "UDP server started", you can move on to the next step. **Feel free to move this file to the desktop to make it easier to start experiments**

- Navigate to the "godot_3.5.2-stable_rpi4_editor.arm64" file in the MouseGoggles/Godot folder. Double-click this file and select "Execute". **Feel free to move this file to the desktop to make it easier to start experiments**

- Import the Godot game project located in MouseGoggles/Godot/MouseVR Godot Project V2.2/project.godot

- With the project highlighted, click "Run"

- Select an experiment (aka "scene")

- A game window will appear with views rendered for each of the two eyepiece displays -- these are rotated to match the rotations of each display and are positioned in the center of the screen -- do not move this window

- By default, forward/backward movement and left/right turning in the VR scene can be controlled by a USB computer mouse or trackpad, which can be used to verify the VR system is correctly working

- Upon the completion of each repetition of an experiment (typically 30 - 60 s duration), logs of the mouse movement and important experiment parameters will be saved in "MouseVR Godot Project V2.2/logs/" in csv format (one row per frame, one column per data type)

- Click the `esc` button to exit an experiment early; the in-progress/unfinished repetition be saved in the final log file

### Operating the system remotely with VNC

- Make sure that the reaspberry Pi is connected to the internet or your local network
* Open up a Raspberry Pi command terminal and enter the following line:
  
  ```
  sudo raspi-config
  ```
- Click on `Interface Options`, then `VNC`, and click `enable`. Save and exit the raspi-config window

- Open up another Raspberry Pi command terminal and enter the following line:
  
  ```
  ifconfig
  ```

- Scroll down and look for the `inet` field. Find the number to the right and write it down for later (e.g. `10.192.168.1`)

- On the PC from which you'd like to control the MouseGoggles system (and which is connected to the same network as the Raspberry Pi), download [RealVNC Viewer](https://www.realvnc.com/en/connect/download/viewer/). From the search bar, enter the Raspberry Pi's `inet` number. When prompted for a username and password, enter the information you set during the Raspberry Pi OS installation

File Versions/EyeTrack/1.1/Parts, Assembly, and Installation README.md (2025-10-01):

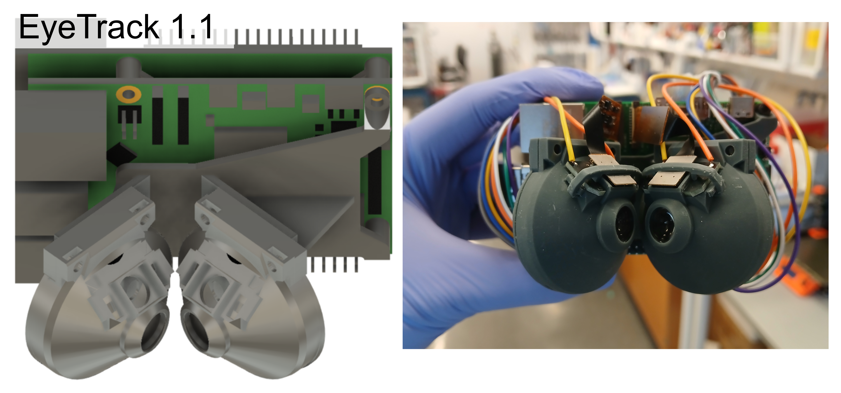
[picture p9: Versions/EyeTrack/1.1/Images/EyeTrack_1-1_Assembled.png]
(left) 3D render of assembled MouseGoggles EyeTrack 1.1. (right) Picture of assembled MouseGoggles EyeTrack 1.1


# 

IMPORTANT July 2025 Update: The miniature infrared eye-tracking cameras used used in this update now appear to be discontinued from Arducam! If you're seeking to build an EyeTrack headset, first try and find an alternative supplier for the IMX519 NoIR camera listed below before proceeding. 

A new version of the EyeTrack headset is currently being developed to use newer cameras and displays: [EyeTrack 1.9](https://github.com/sn-lab/MouseGoggles/tree/main/Versions/EyeTrack/1.9).

# Parts List

---

### Off-the-shelf parts

The table below lists all off-the-shelf parts required to build MouseGoggles EyeTrack 1.1, updated with newer IR-sensitive cameras, dual-camera-support with a Raspberry 5, and a simpler assembly! This system is also the first to use Godot Project 2.1, which enables control of the eye-tracking cameras from within the Godot VR game engine.

Follow the links below to purchase the parts in the quantities listed (though you may considering ordering spare parts as well). In addition to these listed parts, you will also need some basic computer peripherals (HDMI monitor, USB keyboard and mouse /touchpad, microSD card reader), at for the initial setup.

| Part Name                                         | Description                                         | Link                                                                                                                                                            | Est. Unit Cost | Quantity |
| ------------------------------------------------- | --------------------------------------------------- | --------------------------------------------------------------------------------------------------------------------------------------------------------------- |:--------------:|:--------:|
| Raspberry Pi 4 Model B - 2 GB                     | Raspberry Pi 4 Single-board computer                | [PiShop.US](https://www.pishop.us/product/raspberry-pi-4-model-b-2gb/?src=raspberrypihttps://www.pishop.us/product/raspberry-pi-4-model-b-2gb/?src=raspberrypi) | $45            | 1        |
| Raspberry Pi 5/4GB                                | Raspberry Pi 5 Single-board computer                | [PiShop.US](https://www.pishop.us/product/raspberry-pi-5-4gb/)                                                                                                  | $60            | 1        |
| Class 10 - MicroSD Card Extreme Pro - 32 GB       | MicroSD card to Raspberry Pi OS                     | [PiShop.US](https://www.pishop.us/product/class-10-microsd-card-extreme-pro-32-gb-blank-bulk/)                                                                  | $13            | 2        |
| Micro-HDMI to HDMI cable for Pi 4, 3ft, Black     | HDMI adapter to connect Raspberry Pi to monitor     | [PiShop.US](https://www.pishop.us/product/micro-hdmi-to-hdmi-cable-for-pi-4-3ft-black/)                                                                         | $5             | 2        |
| Waveshare 1.28 inch 240x240 display               | Circular display (with 8-pin cable) for VR eyepiece | [Waveshare](https://www.waveshare.com/product/1.28inch-lcd-module.htm)                                                                                          | $15            | 2        |
| FRP0510 - Ø1/2" Fresnel Lens, f = 10 mm           | Fresnel lens for VR headset                         | [Thorlabs](https://www.thorlabs.com/thorproduct.cfm?partnumber=FRP0510)                                                                                         | $21            | 2        |
| FM01 1" Hot mirror                                | Hot mirror for eye tracking camera                  | [Thorlabs](https://www.thorlabs.com/thorProduct.cfm?partNumber=FM01)                                                                                            | $39            | 2        |
| 12" female jumper wires                           | Wires to power IR LED circuit                       | [Adafruit](https://www.adafruit.com/product/793)                                                                                                                | $8             | 1        |
| GPIO Header for Raspberry Pi - 2x20 Female Header | Pin header to connect custom PCB to Pi 4            | [Adafruit](https://www.adafruit.com/product/2222)                                                                                                               | $1.5           | 1        |
| Break-away 0.1" male header strip                 | Pin header to connect wires to custom PCB           | [Adafruit](https://www.adafruit.com/product/392)                                                                                                                | $5             | 1        |
| Raspberry Pi 5 Power Supply                       | USB-C power supply                                  | [Adafruit](https://www.adafruit.com/product/5814)                                                                                                               | $12            | 2        |
| 4-40 thread, 1" length socket head screws         | Pack of 1" long screws to assemble parts            | [McMaster](https://www.mcmaster.com/90044A111/)                                                                                                                 | $9             | 1        |
| 4-40 thread, 1/4" length socket head screws       | Pack of 1/4" long screws to assemble parts          | [McMaster](https://www.mcmaster.com/91251A106/)                                                                                                                 | $12            | 1        |
| 4-40 thread, 3/16" wide narrow hex nuts           | Pack of hex nuts to assemble parts                  | [McMaster](https://www.mcmaster.com/90760A160/)                                                                                                                 | $5             | 1        |
| VSMB2943GX01 SMD 940 nm Infrared LED              | IR LED for eye tracking illumination                | [DigiKey](https://www.digikey.com/en/products/detail/vishay-semiconductor-opto-division/VSMB2943GX01/3984794)                                                   | $0.6           | 4        |
| 100 Ohm SMD Resistor, 0805 package                | Resistor for IR LED circuit                         | [DigiKey](https://www.digikey.com/en/products/detail/yageo/RC0805FR-07100RL/727543)                                                                             | $0.1           | 2        |
| IMX519 NoIR Camera Module for Raspberry Pi 5      | Mini IR-sensitive eye tracking camera               | [Arducam](https://www.arducam.com/product/arducam-mini-16mp-imx519-camera-module-for-raspberry-pi-zero-b0391/)                                                  | $33            | 2        |
| Ethernet CAT6 Cable - 30cm long                   | Ethernet cable for Pi-to-Pi communication           | [Adafruit](https://www.adafruit.com/product/5443)                                                                                                               | $2.50          | 1        |

### 3D prints

The table below lists all custom 3D-printable parts required for MouseGoggles EyeTrack 1.1. Follow the links below for .stl files to print these parts on your own high-resolution 3D printer (recommended layer resolution <=0.2 mm) or to send to a 3D printing service such as [CraftCloud](https://craftcloud3d.com/). 

Notes on print quality: UV-cured resin-based SLA printers (e.g. [Photon Mono X](https://www.anycubic.com/products/photon-mono-x-resin-printer)) can produce adequate and cost-effective parts for MouseGoggles, though resin-based prints can become brittle over time and are often semi-transparent. To reduce stray light from semi-transparent headset prints, parts can be painted with an opaque paint (e.g. [Black 3.0](https://www.culturehustleusa.com/products/black-3-0-the-worlds-blackest-black-acrylic-paint-150ml)). Thermoplastic polymers such as PLA, PETG, or ABS can produce tougher, longer-laster, and more opaque parts, though should only be used for MouseGoggles from high-resolution 3D printers (e.g. [Ultimaker S3](https://ultimaker.com/3d-printers/s-series/ultimaker-s3/)). If you are printing the parts yourself, a [needle file]([McMaster-Carr](https://www.mcmaster.com/4261A37/)) can be helpful in cleaning up any imperfections in the part.

| Part Name                           | Description                                     | Link                                                                                                                                | Quantity | Aprox. Dimensions (mm) |
| ----------------------------------- | ----------------------------------------------- | ----------------------------------------------------------------------------------------------------------------------------------- | -------- | ---------------------- |
| Eyepiece EyeTrack V8 AngleLeft.stl  | Angled-left eyepiece enclosure (for right eye)  | [stl](https://github.com/sn-lab/MouseGoggles/blob/main/Versions/EyeTrack/1.1/3D%20Prints/Eyepiece%20EyeTrack%20V8%20AngleLeft.stl)  | 1        | 44x41x21               |
| Eyepiece EyeTrack V8 AngleRight.stl | Angled-right eyepiece enclosure (for left eye)  | [stl](https://github.com/sn-lab/MouseGoggles/blob/main/Versions/EyeTrack/1.1/3D%20Prints/Eyepiece%20EyeTrack%20V8%20AngleRight.stl) | 1        | 44x41x21               |
| Enclosure Back V3.stl               | Eyepiece enclosure backing                      | [stl](https://github.com/sn-lab/MouseGoggles/blob/main/Versions/EyeTrack/1.1/3D%20Prints/Enclosure%20Back%20V3.stl)                 | 2        | 41x41x8                |
| EyeTrack SpacerA V4.stl             | Mirror-lens spacer for eyepiece                 | [stl](https://github.com/sn-lab/MouseGoggles/blob/main/Versions/EyeTrack/1.1/3D%20Prints/EyeTrack%20SpacerA%20V4.stl)               | 2        | 32x32x10               |
| EyeTrack SpacerB V4.stl             | Display-mirror spacer for eyepiece              | [stl](https://github.com/sn-lab/MouseGoggles/blob/main/Versions/EyeTrack/1.1/3D%20Prints/EyeTrack%20SpacerB%20V4.stl)               | 2        | 32x30x6                |
| Pi5 Mount V1.stl                    | Eyepiece mount for Raspberry Pi 5               | [stl](https://github.com/sn-lab/MouseGoggles/blob/main/Versions/EyeTrack/1.1/3D%20Prints/Pi5%20Mount%20V1.stl)                      | 1        | 79x55x29               |
| Pi Spacer V1                        | Spacer for Raspberry Pi 4 and 5                 | [stl](https://github.com/sn-lab/MouseGoggles/blob/main/Versions/EyeTrack/1.1/3D%20Prints/Pi%20Spacer%20V1.stl)                      | 1        | 64x55x7                |
| Camera Clip V1.stl                  | Clip to secure IR camera and LED board          | [stl](https://github.com/sn-lab/MouseGoggles/blob/main/Versions/EyeTrack/1.1/3D%20Prints/Camera%20Clip%20V1.stl)                    | 2        | 27x9x2                 |
| IMX519 Key V1.stl                   | Adjustment key for changing focus of IR cameras | [stl](https://github.com/sn-lab/MouseGoggles/blob/main/Versions/EyeTrack/1.1/3D%20Prints/IMX519%20Key%20V1.stl)                     | 1        | 15x15x9                |

### Custom PCBs

The table below lists all custom PCBs (printed circuit boards) used by MouseGoggles EyeTrack 1.1. To order a bare custom PCB, you can use a PCB printing service such as [JLCPCB](https://cart.jlcpcb.com/quote?orderType=1&stencilLayer=2&stencilWidth=100&stencilLength=100&stencilCounts=5) or [seeedstudio](https://www.seeedstudio.com/fusion_pcb.html). JLCPCB-prints have been verified for all MouseGoggles PCBs. To order a PCB, follow the links in the table to download the zipper gerber files. Upload the zipped folder to the PCB printing service, set any required PCB parameters (e.g. layers=2, FR-4 board material, 1.6 mm board thickness, 0.0348 mm copper thickness, and HASL with lead surface finish), and choose your desired quantity.

| Part Name                                    | Description                                      | Link                                                                                                                                                                  | Quantity |
| -------------------------------------------- | ------------------------------------------------ | --------------------------------------------------------------------------------------------------------------------------------------------------------------------- | -------- |
| MouseGoggles EyeTrack Hat-1-1_2025-02-03.zip | zipped Gerber files of Rasberry Pi PCB connector | [zip](https://github.com/sn-lab/MouseGoggles/blob/main/Versions/EyeTrack/1.1/PCBs/MouseGoggles%20EyeTrack%20Hat-1-1/MouseGoggles%20EyeTrack%20Hat-1-1_2025-02-03.zip) | 1        |
| MouseGoggles IRLED-1-5_2023-12-21.zip        | zipped Gerber files of IR LED PCB mount          | [zip](https://github.com/sn-lab/MouseGoggles/blob/main/Versions/EyeTrack/1.1/PCBs/MouseGoggles%20IRLED-1-5/MouseGoggles%20IRLED-1-5_2025-02-12.zip)                   | 2        |

# 

# Hardware Assembly Instructions

Image series of MouseGoggles EyeTrack 1.1 assembly process

---

### Assemble the custom PCBs

1. Insert the 2x20 GPIO header onto the back of the "Hat" PCB (the side without any text) and solder the header in place.

2. Break away two 8-pin sections and two 6-pin sections of male headers and insert them onto the front of the custom PCB (the side with text) and solder them in place.

3. Solder a 100 ohm resistor to the central solder pad on each "IRLED" PCB.

4. Solder two IR LEDs onto each IRLED PCB, with the polarity of both LEDs orientated in the same direction.

5. Detach four female jumper wires into two pairs, and strip one end of each to expose one side of the jumper wire pairs. Solder each exposed wire to the corner through-holes of the IRLED PCBs.

### Assemble the MouseGoggles headset

1. With the small end of an "Eyepiece" 3D print facing down, insert a Fresnel lens straight down into the bottom, with the ridged side facing up and the smooth side facing down. 
   
   * Note: very gently sliding your finger or fingernail along each flat face of the lens will tell you which side is smooth and which side is ridged.

2. Insert the "SpacerA" 3D print into the eyepiece, ensuring it is sitting tight up against the lens and the small tabs in the Eyepiece positioned inside the notches of the Spacer.

3. Place the Hotmirror on top of the SpacerA part, so that it sits firmly in the cutout of the part.

4. Insert the "SpacerB" 3D print in top of the hotmirror, ensuring it is sitting tight up against the hot mirror and the small tabs in the SpacerA part are positioned inside the notches of the Spacer.

5. Insert the Waveshare display into the Eyepiece so that it fits snugly inside the enclosure and sits tight up against SpacerB.

6. Slide the "Enclosure Back" 3D print into the back of the Eyepiece, angling it so that the tabs of the Enclosure Back fit inside the notches of the Eyepiece and the screw holes of both parts are lined up.

7. Insert two hex nuts inside the slots of the Eyepiece, and screw two hex screws through the Enclosure Back to secure the eyepiece together.

8. Repeat steps 1-5 to create a second eyepiece.

9. Before inserting the NoIR cameras into the eyepieces, remove the dab of glue on the side of the lens (just inside the square outer case) which prevents adjustment of the camera focus. Dig out the glue using a small tool such as a needle or small pair of scissors, until the lens can be rotated smoothly using the "IMX519 Key" 3D print. After the glue is removed, use the key to unscrew the lens until it protrudes from its square case by ~2 mm.

10. On each eyepiece, place the assembled IRLED PCB into the cutout on the side of the eyepiece enclosure, and insert a NoIR camera into the camera slot. Holding the IRLED PCB and camera in place, slide the "Clip" 3D print over the camera and LED board, bending the clip so that it grabs the ledges of the eyepiece next to the LED boad, securing the camera board in place. 

11. Attach the "Pi5 Mount" 3D print to the top of a Raspberry Pi 5 (the side with the connectors) by lining up the mounting holes and inserting three 1" long screws from the top of the Pi5 Mount. Do not add nuts to the bottom of the Raspberry Pi yet.

12. Connect the "Pi Spacer" 3D print to the bottom of th Raspberry Pi 5, threading the screws through the mounting holes.

13. Connect a Raspberry Pi 4 below the Pi Spacer, so that the bottom of the Pi 4 is next to the bottom of the Pi 5.

14. Add 3 hex nuts to the screws, tightening them to the top of the Pi 4. You may add a 4th screw to the empty through hole if desired.

15. On each eyepiece, insert two hex nuts into the slots of the Enclosure Back, and secure the eyepiece to the Pi 5 mount using hex screws. Orient the eyepieces so that the cameras are nearer the open side of the Pi 5 mount which exposes the pair of CSI camera ports. Repeat for the other eyepiece.
    
    * Note: If any part is too difficult to slide into place, use a needle file to sand down any warped areas or imperfections of the 3D prints. The edges of the custom PCBs can also be sanded down, since there may also be imperfections in the PCB manufacturing/cutting process.

### Wire up the displays and cameras

1. Attach the custom PCB to the Raspberry Pi's 40-pin header, so that the custom PCB hangs over the Pi (rather than hanging off the side).

2. Attach the 8-pin cables to the circular display of each eyepiece.

3. Attach each wire of the 8-pin cable to the matching header on the custom PCB, attaching the right eye to the display0 header and the left-eye to the display1 header. 

4. Attach the camera ribbon cables to the pair of CSI ports on a Raspberry Pi 5.

5. Insert each IRLED PCB's female jumpers into the ground and 5V pins of the Raspberry Pi headers.

# Software Installation Instructions

---

To install all necessary software, you'll first need a PC to install the Raspberry Pi OS to the MicroSD cards that will be installed in the Raspberry Pis. Next, you'll need to start up the Raspberry Pis and install the necessary software. For the Raspberry Pi 4, you will install the Godot game engine and custom display driver, as well as all dependencies listed in the instructions below. For the Raspberry Pi 5, you will install the camera driver and software. Software installation on each Raspberry Pi typically takes <10 minutes.

## Installing software for the Raspberry Pi 4

### Install the Legacy Raspberry Pi 4 Operating System

- Insert a blank micro SD card into your PC
- Download and install the [Raspberry Pi Imager](https://www.raspberrypi.com/software/)
- Choose Device: "Raspiberry Pi 4""
- Choose OS: "Raspberry Pi OS (Legacy, 32-bit)"
- Choose Storage: -select your SD card-
- When asked if you would like to apply custom OS settings, click "Edit Settings"
- Set the hostname, username, password, WiFi, and localisation settings as desired, then click save and exit the settings window
- Select "yes" to install the OS with your custom settings
- After the image has finished writing, Insert the SD card into your Raspberry Pi and power it on

### Install the Godot game engine

- Start the Raspberry Pi and connect to the internet.
  - to connect to a wireless internet network, you will first be asked to set your wireless LAN country
- Open up the githib page for the [Unofficial Godot Engine for the Raspberry Pi](https://github.com/hiulit/Unofficial-Godot-Engine-Raspberry-Pi/tree/main?tab=readme-ov-file#compiling).
- In the "Downloads" section, download the zip file for 3.5.2 - Raspberry Pi 4
- After the zip file has been downloaded, navigate to your "downloads" folder, right-click on the zip file, and click "extract here"
- Inside the unzipped folder, find the "...editor_Ito.bin" file. This is the executable file for running the godot game engine. To run the engine, double-click this file and select "Execute" (you do not need to run the engine yet)

### Install the display driver

- Open up the Raspberry Pi command terminal and enter each line, one at a time:
  
  ```
  sudo apt install python3-opencv
  sudo apt-get install cmake
  cd ~
  git clone https://github.com/sn-lab/MouseGoggles
  cd MouseGoggles/fbcp-ili9341
  mkdir build
  cd build
  cmake -DGC9A01=ON ..
  make -j
  sudo ./fbcp-ili9341
  ```

- note 1: When you are asked if you want to continue installing, answer yes.

- note 2: See the error "vc_dispmanx_display_open failed!" on the last step? See [this issue](https://github.com/sn-lab/MouseGoggles/issues/23) for a quick fix.

This installation has been verified using the following software versions:

- flatpak: 1.14.1-4
- cmake: cmake-3.27.4
- unofficial godot: 3.5.2-stable

## Installing Software for the Raspberry Pi 5
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

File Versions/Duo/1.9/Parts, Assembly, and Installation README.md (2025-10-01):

(left) 3D render of assembled MouseGoggles EyeTrack 1.1. (right) Picture of assembled MouseGoggles EyeTrack 1.1

# 

**NOTE:** This version is currently in development and is subject to change; if you proceed with building this version and notice any mistakes or problems, raise an issue on Github!

# Parts List

---

### Off-the-shelf parts

The table below lists all off-the-shelf parts required to build MouseGoggles Duo 1.9, a complete re-design of the Duo headset featuring newer, longer-lasting parts and a simpler assembly and installation process!
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

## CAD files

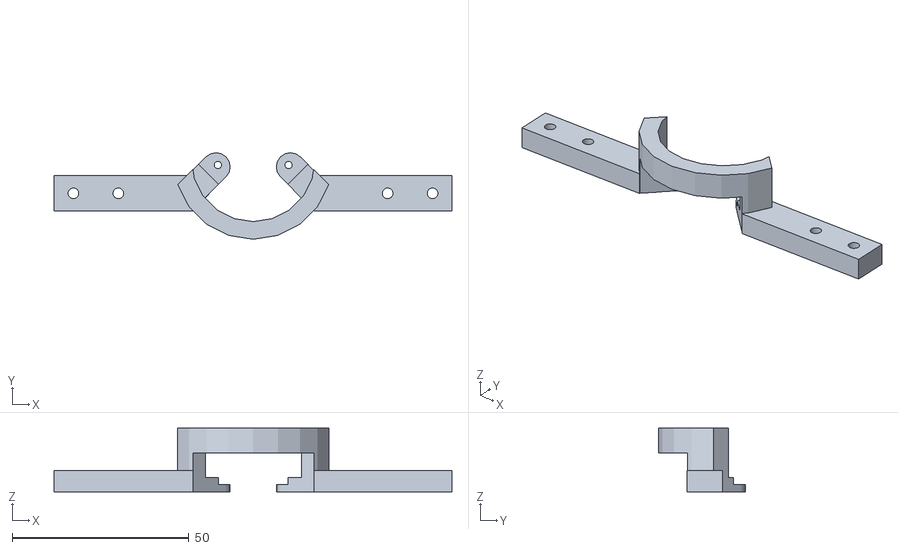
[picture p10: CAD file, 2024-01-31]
Other Hardware/Headbars/SN HeadbarMount V2.stl
112.6 x 24.5 x 18.0

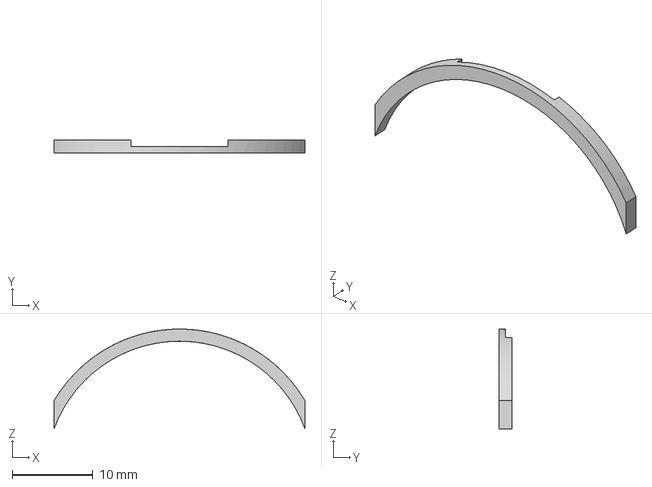
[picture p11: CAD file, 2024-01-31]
Versions/Duo/1.0/3D Prints/MouseGoggles 1.0 DisplayHolderV1.step
31.0 x 1.55 x 12.3 mm

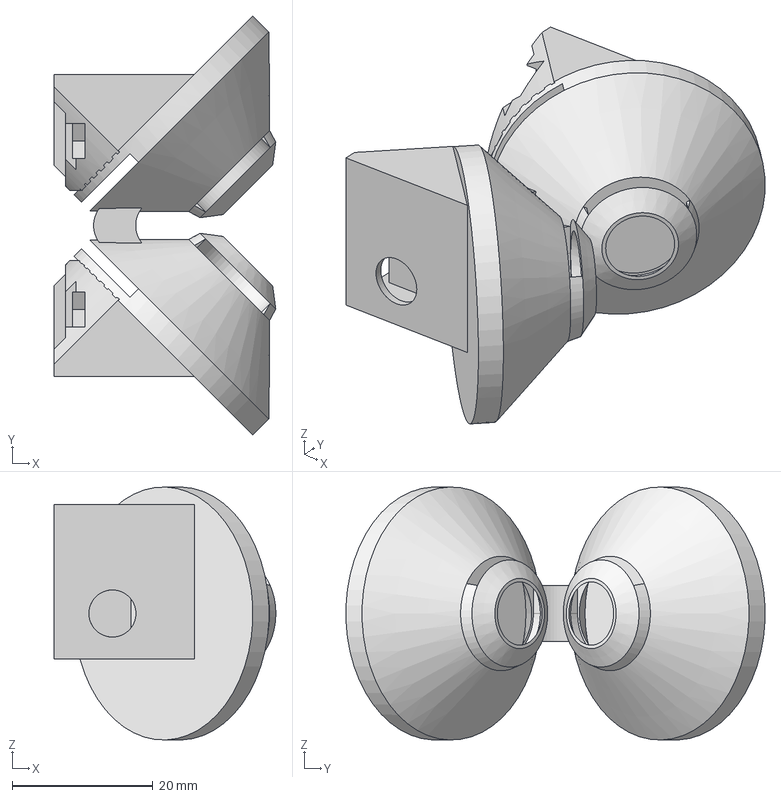
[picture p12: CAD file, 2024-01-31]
Versions/Duo/1.1/3D Prints/MouseGoggles 1.1 HeadsetV1.step
31.5 x 59.6 x 36.0 mm
MouseEyepieceRight_bare v3
MouseEyepieceLeft_bare v3

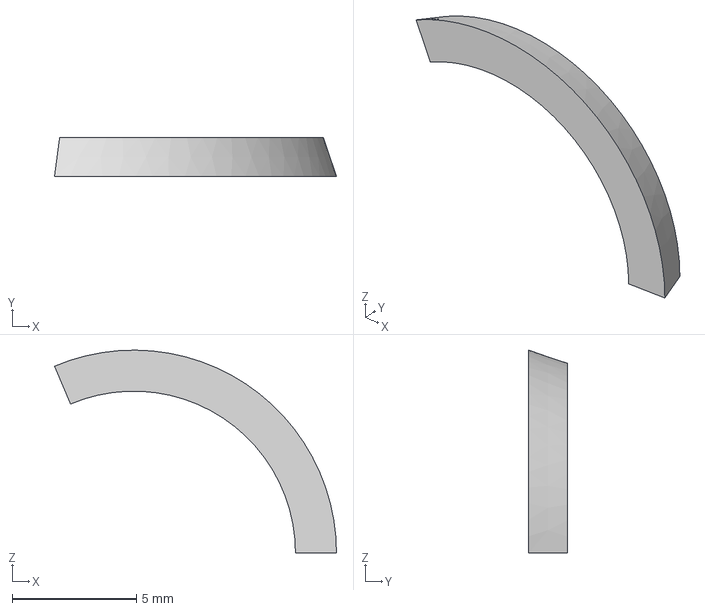
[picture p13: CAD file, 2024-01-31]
Versions/Duo/1.3/3D Prints/MouseGoggles 1.0 LensHolderV1.step
11.3 x 1.55 x 8.15 mm

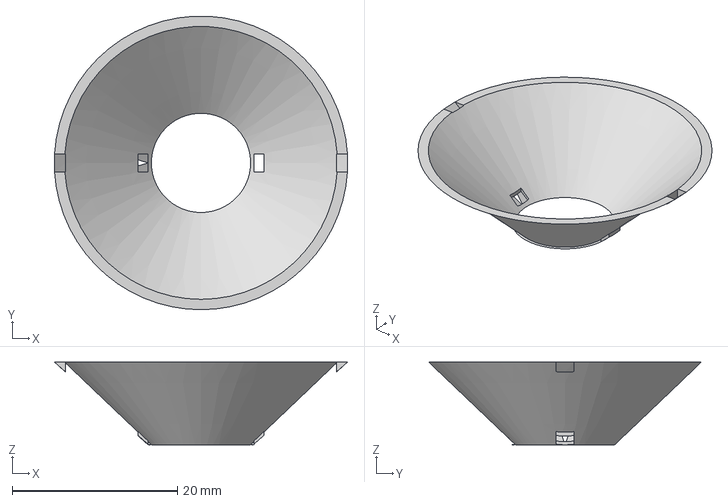
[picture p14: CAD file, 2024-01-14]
Versions/Duo/1.5/3D Prints/MouseGoggles 1.5 EyepieceSpacerV2.step
35.4 x 35.5 x 10.0 mm

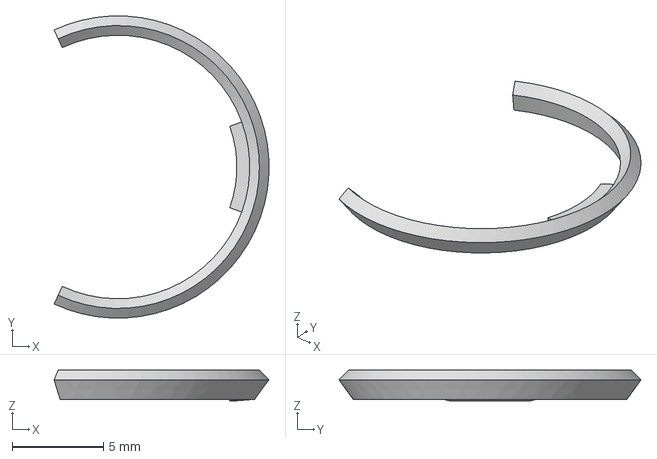
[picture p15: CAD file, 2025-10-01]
Versions/Duo/1.9/3D Prints/LensClip 2.0 V1.step
11.7 x 16.5 x 1.67 mm

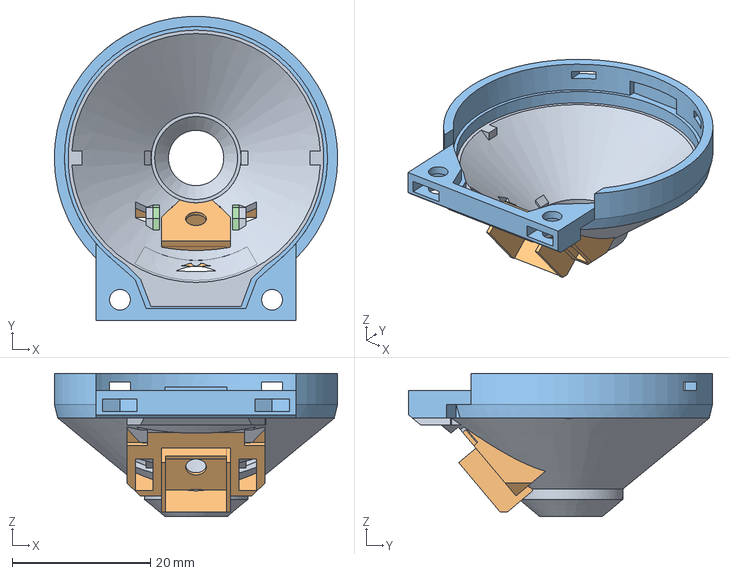
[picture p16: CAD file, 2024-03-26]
Versions/EyeTrack/1.0/3D Prints/EyeTrack 1.0 EyepieceEnclosureV6.step
41.0 x 44.0 x 20.8 mm
Eye-R module V4 v5

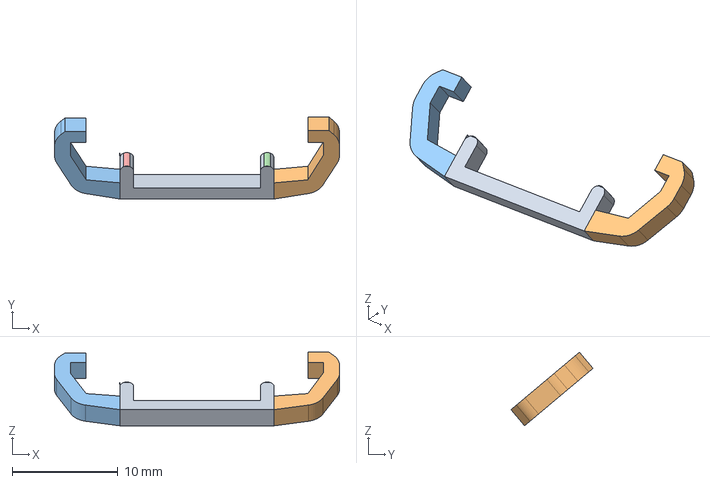
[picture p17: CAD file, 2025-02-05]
Versions/EyeTrack/1.1/3D Prints/Camera Clip V1.step
27.0 x 7.78 x 6.98 mm

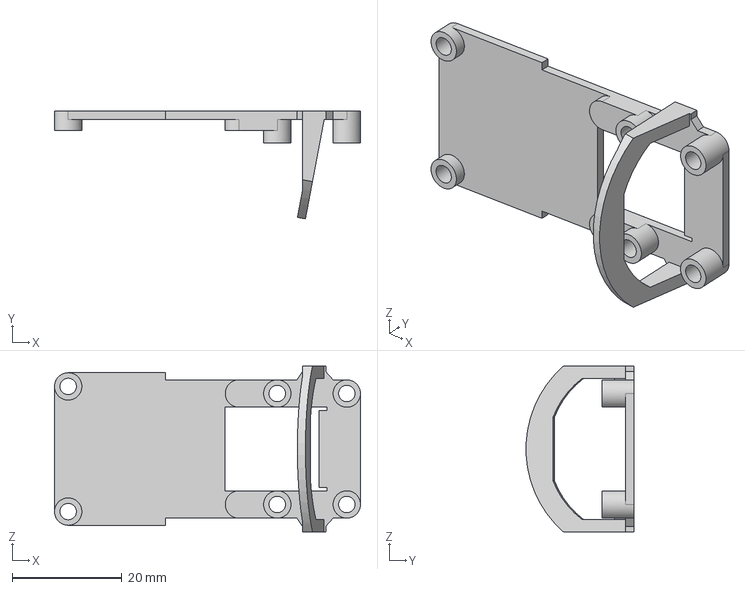
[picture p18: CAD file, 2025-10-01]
Versions/EyeTrack/1.9/3D Prints/EyepieceCamBack 2.0 V1.step
55.9 x 19.7 x 30.3 mm

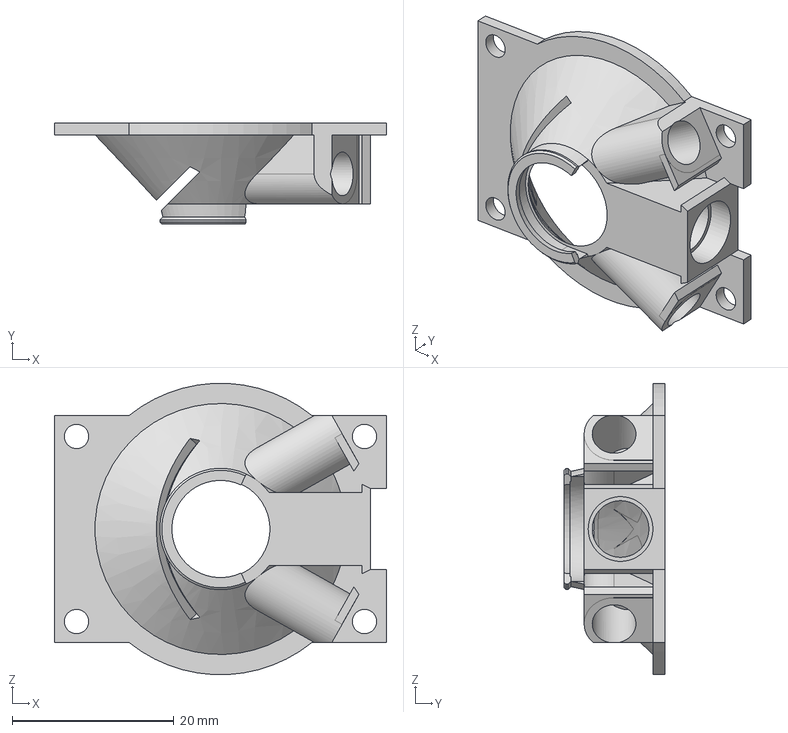
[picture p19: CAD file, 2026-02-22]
Versions/EyeTrack/2.0/3D Prints/Eyepiece V2.step
41.0 x 12.5 x 36.0 mm

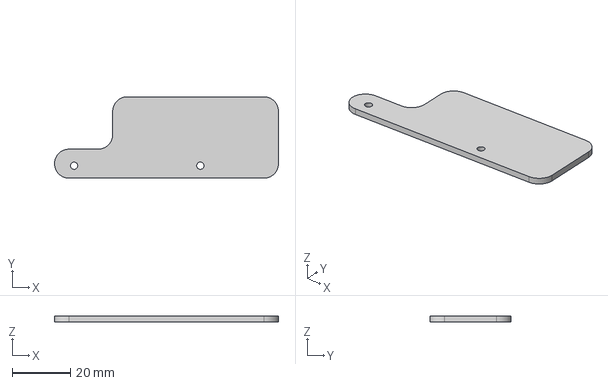
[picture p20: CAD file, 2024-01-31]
Other Hardware/Headbars/SN LinearTreadmillWall V4.step
77.0 x 28.0 x 2.00 mm

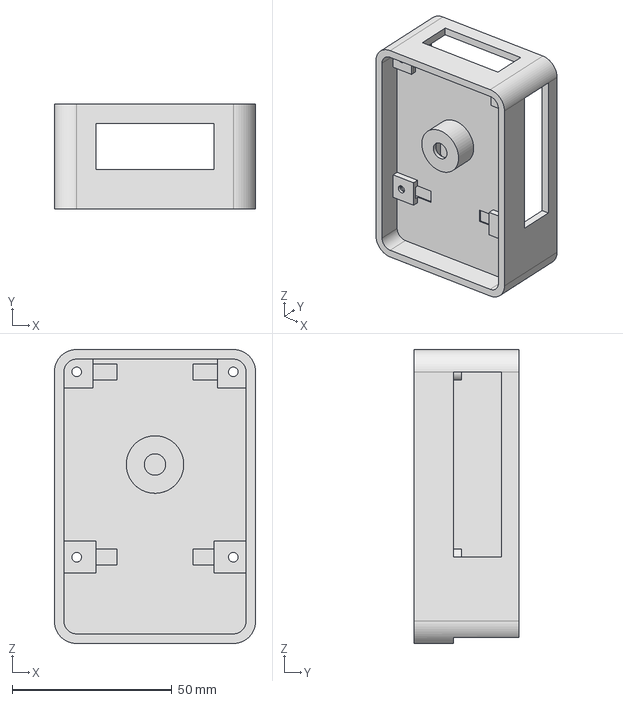
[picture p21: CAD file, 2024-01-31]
Versions/Duo/1.0/3D Prints/MouseGoggles 1.0 RaspberryPiCaseBackV4.step
63.0 x 33.0 x 92.0 mm

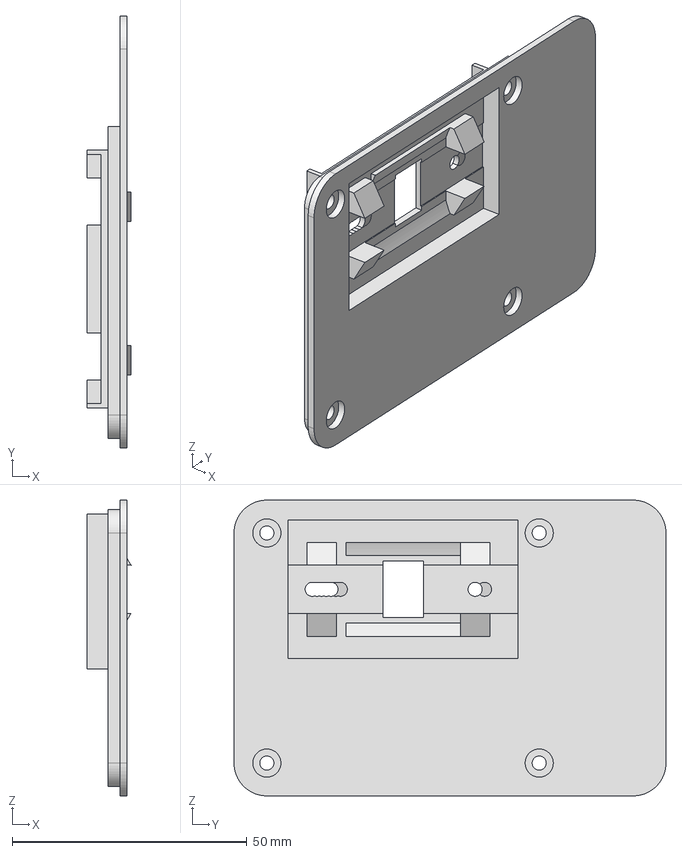
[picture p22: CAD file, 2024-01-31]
Versions/Duo/1.3/3D Prints/MouseGoggles 1.3 RaspberryPiCaseFrontPanelV2.step
9.38 x 92.0 x 63.0 mm

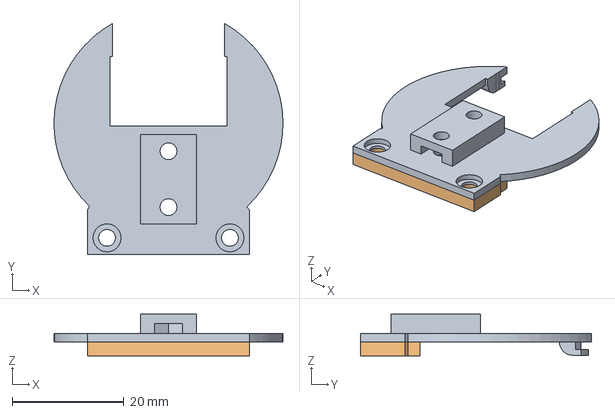
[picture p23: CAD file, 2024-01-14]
Versions/Duo/1.5/3D Prints/MouseGoggles 1.5 EyepieceEnclosureBackV2.step
41.0 x 41.4 x 7.50 mm

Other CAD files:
Versions/Duo/1.2/3D Prints/MouseGoggles 1.2 EyepieceRightV2.step
Versions/Duo/1.2/3D Prints/MouseGoggles 1.2 EyepieceLeftV2.step
Other Hardware/Headbars/SN Headbar V1.step
Other Hardware/Headbars/SN Headbar V1.stl
Other Hardware/Headbars/SN HeadbarMount V2.dwg
Other Hardware/Headbars/SN HeadbarMount V2.ipt
Other Hardware/Headbars/SN HeadbarMountBlock V2.step
Other Hardware/Headbars/SN HeadbarMountBlock V2.stl
Other Hardware/Headbars/SN LinearTreadmillWall V4.stl
Versions/Duo/1.0/3D Prints/MouseGoggles 1.0 DisplayHolderV1.stl
Versions/Duo/1.0/3D Prints/MouseGoggles 1.0 LensHolderV1.stl
Versions/Duo/1.0/3D Prints/MouseGoggles 1.0 RaspberryPiCaseBackV4.stl
Versions/Duo/1.0/3D Prints/MouseGoggles 1.0 RaspberryPiCaseFrontV4.step
Versions/Duo/1.0/3D Prints/MouseGoggles 1.0 RaspberryPiCaseFrontV4.stl
Versions/Duo/1.1/3D Prints/MouseGoggles 1.0 DisplayHolderV1.stl
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

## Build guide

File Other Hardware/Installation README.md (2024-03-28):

This document contains installation instructions for code to read treadmill motion and transmit this data in the format expected by the MouseGoggles Godot game engine. Software support for two different treadmill systems is described -- one spherical and one linear -- though many more treadmill systems can easily be supported simply by adapting the treadmill motion detection system to output motion in the format of computer mouse emulation, as the code linked below does. For building or purchasing the required treadmill hardware, see the links in each treadmill section. For a description of headbars and mounts that can head-fix a mouse above these treadmills while still leaving enought space for a MouseGoggles Headset, see the section at the bottom.

# Spherical Treadmill

The spherical treadmill system used with MouseGoggles is based on an open design originally described [here](https://pubmed.ncbi.nlm.nih.gov/19829374/). This treadmill simulates 2D navigation to a head-fixed mouse, allowing ground translation and yaw rotation. The treadmill motion is measured using two optical flow sensors pointed at the treadmill along orthogonal axes, with sensor data acquired by an Arduino Due micrcontroller. To be compatabile with MouseGoggles, the microcontroller code should be customized to convert these two sources of horizontal and vertical optic flow into treadmill spherical rotations: yaw, pitch, and roll. These rotation values are then sent to the Raspberry Pi over USB through computer mouse emulation: yaw rotations mapped as mouse x movement, pitch as mouse y movement, and roll as mouse scroll wheel movement. Follow the instructions below to upload the [ADNS3080_Mouse_Controller_V5.ino](https://github.com/sn-lab/MouseGoggles/blob/main/Other%20Hardware/Spherical%20Treadmill/ADNS3080_Mouse_Controller_V5/ADNS3080_Mouse_Controller_V5.ino) Arduino code to the treadmill microcontroller.

- Download the latest [Arduino IDE](https://www.arduino.cc/en/software) on your PC/laptop

- In the Arduino IDE, load the ADNS3080_Mouse_Controller_V5.ino script.

- Plug in the treadmill microcontroller to your PC with a microUSB-USB cable. On the Ardunio Due, Use the [Programming Serial USB](https://wiki-content.arduino.cc/en/Guide/ArduinoDue).

- In `Tools>Board`, select `Arduino ARM (32-bits) Boards>Arduino Due (Programming Port)`

- In `Tools>USB Type`, select `Keyboard+Mouse+Joystick`

- In `Tools>Port`, select the serial port the microcontroller is connected to (if you're not sure, disconnect and reconnect the microcontroller to see which COM port changes)

- Click the check mark on the upper left side of the window to verify/compile the sketch, then click the arrow button next to it to upload the code to the microcontroller.

- After the code has been uploaded, plug in the Arduino due to a PC or Raspberry Pi, using the Due's [Native Serial USB](https://wiki-content.arduino.cc/en/Guide/ArduinoDue).

- To verify that the treadmill was successfully reprogrammed, spin the treadmill forward and backward (pitch) to see the computer mouse cursor move up and down; turn the treadmill CW/CCW (yaw) to move the cursor left and right, and spin the treadmill left and right (roll) to move a scroll wheel.
  
  ### Troubleshooting the motion detection system:
  
  The optical sensors used by the spherical treadmill require careful IR illumination of the spherical treadmill in order to successfully detect ball motion. To check the optical sensors' image quality of the treadmill, debugging code is available in the [ADNS3080 Debugging](https://github.com/sn-lab/MouseGoggles/tree/main/Other%20Hardware/Spherical%20Treadmill/ADNS3080%20Debugging) folder. Follow the instructions below to use this debugging software:
  
  * Following the instructions above for uploading code to the Arduino, upload the `MouseCamImages.ino` code (`Tools>USB Type` does not need to be specified).
  
  * Using a Python IDE (Python can be downloaded [here]([Download Python | Python.org](https://www.python.org/downloads/))), open the `mousecam_images.py` script. Edit the `serial_port_name`for the COM port your Arduino is connected to (e.g. "COM5").
  
  * Run the python script in the editor. A window will pop up displaying raw images streamed from the optical sensors. Use these images to adjust your lighting/focus until the treadmill surface texture can be clearly detected.
  
  * After the image quality has been verified, open the `mousecam_motion.py` script, edit the COM port, and run the script. I window will pop up displaying the pattern of optical flow detected from treadmill motion. Use this information to verify that the sensors are successfully detecting motion of the treadmill.

# Linear Treadmill

The linear treadmill system used for MouseGoggles is the low-friction, small foorprint treadmill designed at the Janelia Research Campus described [here]([Low-Friction Rodent-Driven Belt Treadmill | Janelia Research Campus](https://www.janelia.org/open-science/low-friction-rodent-driven-belt-treadmill)). The system can be assembled using design files and instructions on [GitHub]([GitHub - janelia-experimental-technology/Rodent-Belt-Treadmill: Low friction belt treadmill for use in space constrained experimental rigs](https://github.com/janelia-experimental-technology/Rodent-Belt-Treadmill)), or can be purchased fully assembled from [LabMaker]([Mouse Treadmill with Encoder - LABmaker](https://www.labmaker.org/products/mouse-treadmill-with-encoder)). Out of the box, the linear treadmill calculates treadmill speed and direction and outputs their analog values which can be read from the SMA connectors from the attached microcontroller. To convert the microcontroller code to work with MouseGoggles (which reads treadmill motion over USB from computer mouse emulation), follow the instructions below to upload the [LinearTreadmill_Mouse_Controller_V2.ino](https://github.com/sn-lab/MouseGoggles/blob/main/Other%20Hardware/Linear%20Treadmill/LinearTreadmill_Mouse_Controller_V2/LinearTreadmill_Mouse_Controller_V2.ino) Arduino code to the treadmill's microcontroller and plug in the treadmill to the Raspberry Pi with a microUSB-to-USB cable (included from LabMaker).

- Download the latest [Arduino IDE](https://www.arduino.cc/en/software) on your PC/laptop.

- Open up the Arduino IDE, and click File > Preferences (on MacOS, click Arduino IDE > Settings). In "Additional boards manager URLs", copy this link:
  
  `https://www.pjrc.com/teensy/package_teensy_index.json`

- In the main Arduino window, open Boards Manager by clicking the left-side board icon. Search for "teensy", and click "Install".

- In the Arduino IDE, load the `LinearTreadmill_Mouse_Controller_V2.ino` script.

- Plug in the treadmill microcontroller to your PC with a microUSB-USB cable.

- In `Tools>Board`, select `Teensyduino>Teensy LC`.

- In `Tools>USB Type`, select `Keyboard+Mouse+Joystick`.

- In `Tools>Port`, select the serial port the microcontroller is connected to (if you're not sure, disconnect and reconnect the microcontroller to see which COM port changes).

- Click the check mark on the upper left side of the window to verify/compile the sketch, then click the arrow button next to it to upload the code to the microcontroller.

- The Teensyduino program window will automatically open. If Teensyduino prompts you to reset or put the microcontroller in programming mode, click the reset button using a paperclip through the small hole in the plastic microcontroller enclosure.

- To verify that the treadmill was successfully reprogrammed, move the treadmill forward and backward to see the computer mouse cursor move up and down.

# Headbars and Mounts

Using the spherical or linear treadmill requires securing a headbar to the mouse skull and attaching it to a stable mount above the treadmill. For compatability with MouseGoggles, the headbar and mount must leave adequate space around the mouse's eyes. In the [Headbars](https://github.com/sn-lab/MouseGoggles/tree/main/Other%20Hardware/Headbars) folder, design files are supplied for a suitable headbar and mount for each of these treadmill systems. See the details below for instructions in how to obtain these parts. To secure a headbar to a mount, use [1/4" length 4-40 screws](https://www.mcmaster.com/93615A110/)).

### Headbar

The headbar (SN Headbar V1) should ideally be made from titanium to achieve the strength and stiffness neccessary to hold the mouse without breaking, so this part should be ordered from a manufacturer capable of creating titanium parts. To order this part through [emachineshop](), upload the SN Headbar V1.step file and specify the material as "Titanium Grade 2".

### Headbar Mount for the Spherical Treadmill

The headbar mount for the spherical treadmill (SN HeadbarMountBlock V2) can be 3D printed using a thermoplastic with relatively high strength and stiffness, such as PLA. To position this mount above the linear treadmill, the mount can be attached to a [Thorlabs construction cube](https://www.thorlabs.com/thorproduct.cfm?partnumber=RM1F), which can then be attached to [Thorlabs 1/2" optical posts](https://www.thorlabs.com/navigation.cfm?guide_id=52) and mounts.

### Headbar Mount for the Linear Treadmill

The headbar mount for the linear treadmill (SN HeadbarMount V2) should be machined from a relatively stiff metal material, such as stainless steel, which can be manufactured by many machine shops with the supplied SN HeadbarMount V2.ipt design file and SN HeadbarMount V2.dwg schematic file. To position this mount above the linear treadmill, the mount can be attached to [Thorlabs mini-series optical posts](https://www.thorlabs.com/navigation.cfm?guide_id=2249) positioned on either side of the treadmill. The mount position may be blocked by the removable walls of the linear treadmill, so a new design for a treadmill wall and is included in the folder (SN LinearTreadmillWall V4) that can be 3D printed to replace the standard treadmill walls. Walls may also be removed altogether, but can be helpful in training mice to maintain a centered walking position on the treadmill.

# Rotation Sensors

Since MouseGoggles is built in a small form-factor, it is possible to design rotating setups where the headset can rotate with a head-fixed mouse. In such setups, it may be desirable for the experiment to update the mouse's virtual position based on the current rotational position of the headset. To track the headset orientation in real time, an accelerometer can be used to track the roll and/or pitch tilt angles of the headset, while a magnetometer can track the yaw position. In the [Rotation Sensors](https://github.com/sn-lab/MouseGoggles/tree/main/Other%20Hardware/Rotation%20Sensors) folder, two example Arduino programs (written to be run on a Teensy 4.0 microcontroller) are shown which can acquire signals from IIC-based magnetometer or acceleromater sensors, convert those signals to a rotational position, and send this position to a MouseGoggles headset. To build this system, follow the instructions below to purchase the required hardware, install the Arduino software, and test the system with MouseGoggles.

### Parts list

| Part Name                     | Description                                 | Link                                                | Est. Unit Cost | Quantity |
| ----------------------------- | ------------------------------------------- | --------------------------------------------------- | -------------- | -------- |
| (choose 1) LSM6DSOX           | 6 DoF Gyroscope and Accelerometer           | [Adafruit](https://www.adafruit.com/product/4438)   | $12            | 1        |
| (choose 1) LIS3MDL            | Triple-axis Magnetometer                    | [Adafruit](https://www.adafruit.com/product/4479)   | $10            | 1        |
| (choose 1) LSM6DSOX + LIS3MDL | 9 DoF Gyro, Accelerometer, and Magnetometer | [Adafruit](https://www.adafruit.com/product/4517)   | $20            | 1        |
| IIC cable                     | 100 mm length 4-pin Stemma QT cable         | [Adafruit](https://www.adafruit.com/product/4210)   | $1             | 1        |
| Qwiic adapter                 | IIC cable breakout                          | [Sparkfun](https://www.sparkfun.com/products/14495) | $1.6           | 1        |
| Teensy 4.0                    | High -speed microcontroller                 | [PJRC](https://www.pjrc.com/store/teensy40.html)    | $24            | 1        |
| Micro USB/USB A cable         | USB cable to Teensy 4.0                     | [Adafruit](https://www.adafruit.com/product/2185)   | $5             | 1        |
| Pin headers                   | Break-away pin headers (male, short)        | [Adafruit](https://www.adafruit.com/product/3009)   | $5             | 1        |
| Jumper wires                  | 3 inch length female-female jumper wires    | [Adafruit](https://www.adafruit.com/product/1951)   | $2             | 1        |

### Hardware installation

* Solder pin headers onto the Teensy 4.0 and the Qwiic adapter.

* Wire the Teensy to the Qwiic adapter using jumper wires, connecting the 3V and GND cables together, and connecting the SDA and SCL pins of the adapter to pins 18 and 19 of the Teensy, respectively.

* Connect the Sensor to the Qwiic adapter with the IIC cable.

### Software Installation

To install microcontroller code to read sensor signals and transmit rotation values to the MouseGoggles system, follow the instructions below to upload either the [MouseGoggles_Gyro.ino](https://github.com/sn-lab/MouseGoggles/tree/main/Other%20Hardware/Rotation%20Sensors/MouseGoggles_Gyro) (for accelerometer-based roll or pitch control using the LSM6DSOX sensor) or the [MouseGoggles_Magnetometer.ino](https://github.com/sn-lab/MouseGoggles/tree/main/Other%20Hardware/Rotation%20Sensors/MouseGoggles_Magnetometer) Arduino code (for yaw-based control using the LIS3MDL sensor) to the Teensy 4.0 microcontroller and plug the microcontroller into the Raspberry Pi with a microUSB-to-USB cable.

- Download the latest [Arduino IDE](https://www.arduino.cc/en/software) on your PC/laptop.

- Open up the Arduino IDE, and click File > Preferences (on MacOS, click Arduino IDE > Settings). In "Additional boards manager URLs", copy this link:
  
  `https://www.pjrc.com/teensy/package_teensy_index.json`

- In the main Arduino window, open Boards Manager by clicking the left-side board icon. Search for "teensy", and click "Install".

- In the Arduino IDE, load either the `MouseGoggles_Gyro.ino` or the `MouseGoggles_Magnetometer.ino`script.

- Plug in the microcontroller to your PC with a microUSB-USB cable.

- In `Tools>Board`, select `Teensyduino>Teensy LC`.

- In `Tools>USB Type`, select `Keyboard+Mouse+Joystick`.

- In `Tools>Port`, select the serial port the microcontroller is connected to (if you're not sure, disconnect and reconnect the microcontroller to see which COM port changes).

- Click the check mark on the upper left side of the window to verify/compile the sketch, then click the arrow button next to it to upload the code to the microcontroller.

- The Teensyduino program window will automatically open. If Teensyduino prompts you to reset or put the microcontroller in programming mode, click the reset button on the microcontroller.

- To verify that the Teensy was successfully reprogrammed, rotate the sensor in different directions to see the computer mouse cursor move.

### Testing

To verify that the sensor is operating correctly, open the `MouseVR Godot Project V1.6` project in the Godot editor and open the `rotations.gd` script. At the top of the script, specify the type of rotational sensor-control you will be using, defined by the `rotation_type` variable (for yaw, pitch, or roll control). Run the project by clicking the green "play" arrow on the top-right of the editor. Select the `rotations` scene in the scene select window, and verify that rotating the sensor results in a similar rotation in the virtual scene. 

note: you may need to determine through trial-and-error what is the best starting orientation of the sensor to produce the most accurate rotation detection.

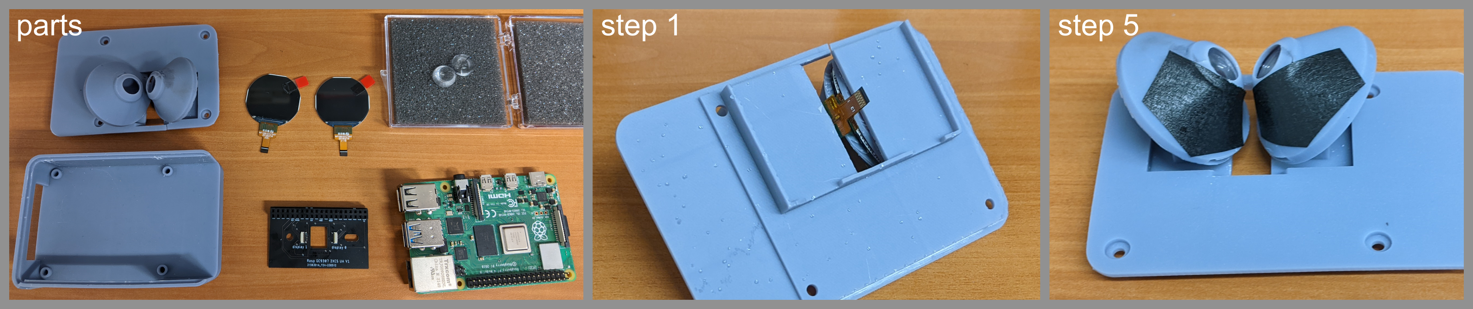
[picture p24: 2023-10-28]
Images/MouseGoggles assembly combined 1.png

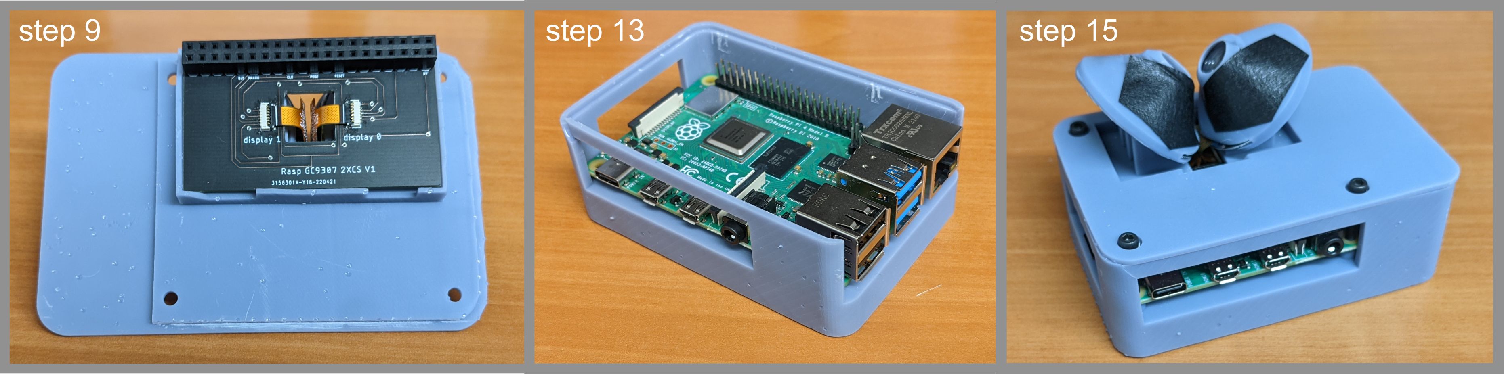
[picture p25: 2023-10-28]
Images/MouseGoggles Assembly combined 2.png

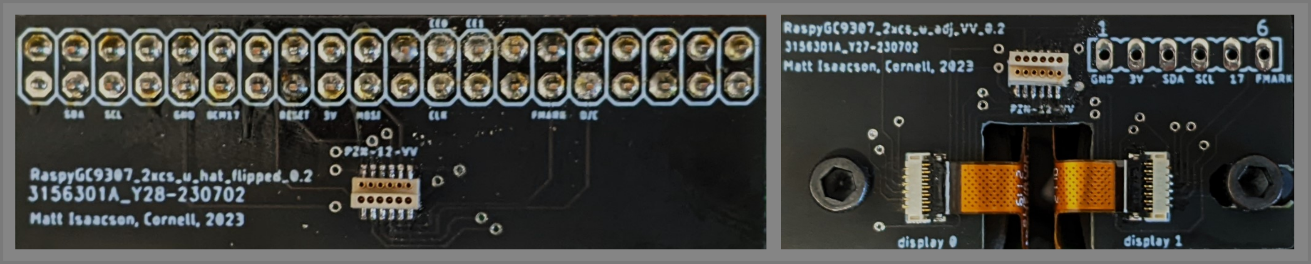
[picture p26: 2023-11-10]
Images/MiniHeadsetPCBsAssembled.png

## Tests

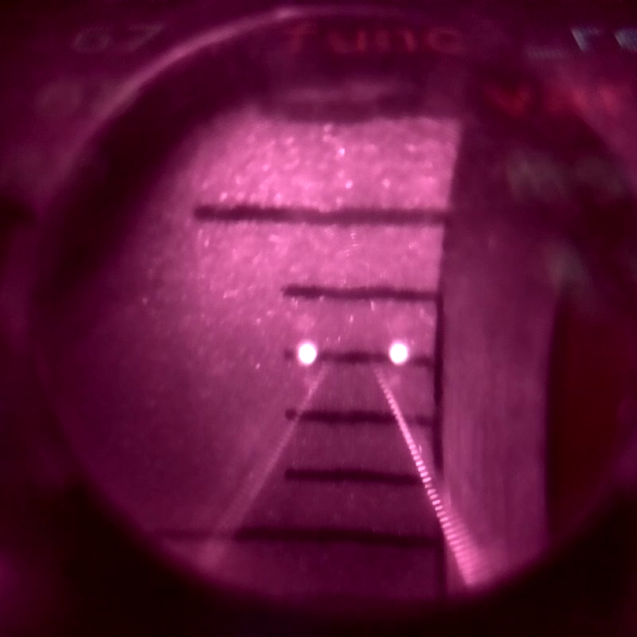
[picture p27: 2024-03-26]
Published Data/Eye Tracking/Camera calibration/right calibration.png

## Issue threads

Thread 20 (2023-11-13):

### ISSUE TITLE
Installing problem

### ISSUE THREAD

**Issue by Tevin-yue** [sn-lab/MouseGoggles#20]
Hi, it is a wonderful project and thanks for your sharing. I met some problems with installing when I followed this project. I have tried the version of raspberry with legacy, 32 bit or 64 bit, but the Godot engine can not open correctly. I wanna to know which version of raspberry and godotengine are compatible to run the  project. Also ,the circular display are not sold anymore, so I have to change the display that satisfy the driver.

**Comment by misaacson01** [comment]
Hello Tevin

flatpak install flathub org.godotengine.Godot3

**Comment by Tevin-yue** [comment]
Hello, I have tried your solution, it seems that I still got something wrong. The error infromation is attached.

As for display, I am still looking for the proper one.

![error1](https://github.com/sn-lab/MouseGoggles/assets/80507794/19a41172-1d85-453f-9ad5-93098142cc0e)
![error2](https://github.com/sn-lab/MouseGoggles/assets/80507794/b931bf57-bc7b-4a78-a034-b1617c9f4252)

**Comment by Tevin-yue** [comment]
Now, I have added an HDMI screen and it is working. However, it seems that the VNC view from SSH has a problem. I have encountered other problems as well:

1. Once I install the driver, Godot can no longer open.

2. I've noticed that the reset and cs pin settings in the config.h file are different from the defined pins used on the Raspberry Pi, according to the PowerPoint file in the hardware.

It would be kind of you to provide some suggestions. Thanks a lot.

**Comment by misaacson01** [comment]
I am not sure about the VNC question, I personally haven't used it with this system. Probably best to first get it working without VNC.

1. After installing and starting the driver, I assume you're opening up a new command window to run Godot? What happens exactly when you try to run Godot? If you can, let me know of any error messages you see, and also the details of your system and installation (whether you're installing ili9341 or st7789; which Raspberry Pi board you're using and where you bought it; what OS version you've installed; which Godot version you've installed).

2. [This graphic](https://www.etechnophiles.com/wp-content/uploads/2020/12/R-Pi-3-B-Pinout.jpg) should explain the differences, the Raspberry Pi has a specific pin naming system but it should all be connected correctly in the PCB and named correctly in the software.

**Comment by misaacson01** [comment]
@Tevin-yue This may have been from a comment that was deleted because the issue has been resolved, but I noticed a new display that appears to be this waveshare display: https://www.waveshare.com/product/1.28inch-lcd-module.htm
In the case that you're trying out this display, I just wanted to let you know that I'm also testing this display (which uses a new GC9A01 chip) and recently wrote a new driver that works for it, so let me know if you'd like it!

**Comment by monrky** [comment]
hi matthew! i am also experiencing a similar godot installation issue - i had to reset our raspberry pi for other reasons (i believe we are still using duo 1.0? or whatever the first version is).  

```
vrpi@raspberrypi:~ $ flatpak install flathub org.godotengine.Godot
Looking for matches…
error: Nothing matches org.godotengine.Godot in remote flathub
vrpi@raspberrypi:~ $ flatpak install flathub org.godotengine.Godot3

Looking for matches…
error: Nothing matches org.godotengine.Godot3 in remote flathub


```

i've also tried downloading it online directly from flathub, but i'm unsure what to do with the file once downloaded 

any help you can offer would be very appreciated!! thanks for all your help :)

**Comment by misaacson01** [comment]
Hi @monrky!

I think there have been some changes to the flathub Godot, on the whole it's a little unstable. I've more recently switched to a different host/version of Godot, which has been working great and doesn't require flatpak at all. Downloading and running it is a little different, but it's very simple. This is what it being used for all our latest headsets. Here is the instructions for installing and running this version of Godot: (taken from EyeTrack v.1.1 installation instructions)

**Install the Godot game engine**

- Start the Raspberry Pi and connect to the internet.
- Open up the github page for the [Unofficial Godot Engine for the Raspberry Pi](https://github.com/hiulit/Unofficial-Godot-Engine-Raspberry-Pi/tree/main?tab=readme-ov-file#compiling).
- In the "Downloads" section, download the zip file for 3.5.2 - Raspberry Pi 4
- After the zip file has been downloaded, navigate to your "downloads" folder, right-click on the zip file, and click "extract here"
- Inside the unzipped folder, find the "...editor_Ito.bin" file. This is the executable file for running the godot game engine. To run the engine, double-click this file and select "Execute".


After you install this version of Godot, if you are using Duo 1.0, you'll still have to use the earlier Godot projects as the newer ones (e.g. Godot project 2.0, used by EyeTrack 1.1) are made for newer displays. But I'm sure you've made changes to the Godot project you were using before and are planning to copy that to the new system.

Let me know how this goes!

**Comment by monrky** [comment]
Works great! thanks!!

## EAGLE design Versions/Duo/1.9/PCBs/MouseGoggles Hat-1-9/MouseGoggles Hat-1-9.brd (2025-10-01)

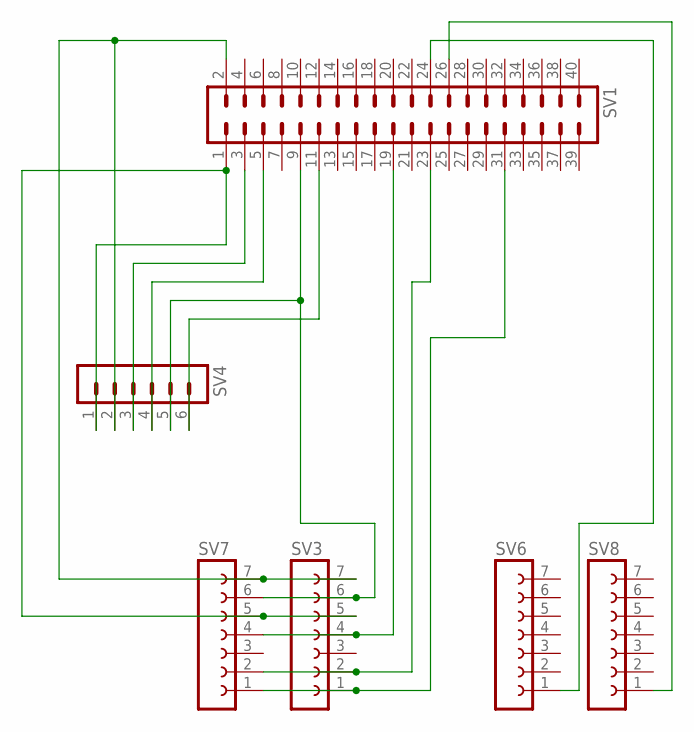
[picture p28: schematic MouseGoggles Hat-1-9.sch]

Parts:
SV1: MA20-2
SV3, SV6, SV7, SV8: FE07-1; FE07
SV4: MA06-1

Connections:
unnamed: SV1.1, SV3.5, SV4.1, SV7.5
unnamed: SV1.9, SV3.6, SV4.5, SV7.6
unnamed: SV1.23, SV3.2, SV7.2
unnamed: SV1.24, SV6.1
unnamed: SV1.26, SV8.1
unnamed: SV1.31, SV3.1, SV7.1
unnamed: SV1.19, SV3.4, SV7.4
unnamed: SV1.3, SV4.3
unnamed: SV1.5, SV4.4
unnamed: SV1.11, SV4.6
unnamed: SV1.2, SV3.7, SV4.2, SV7.7

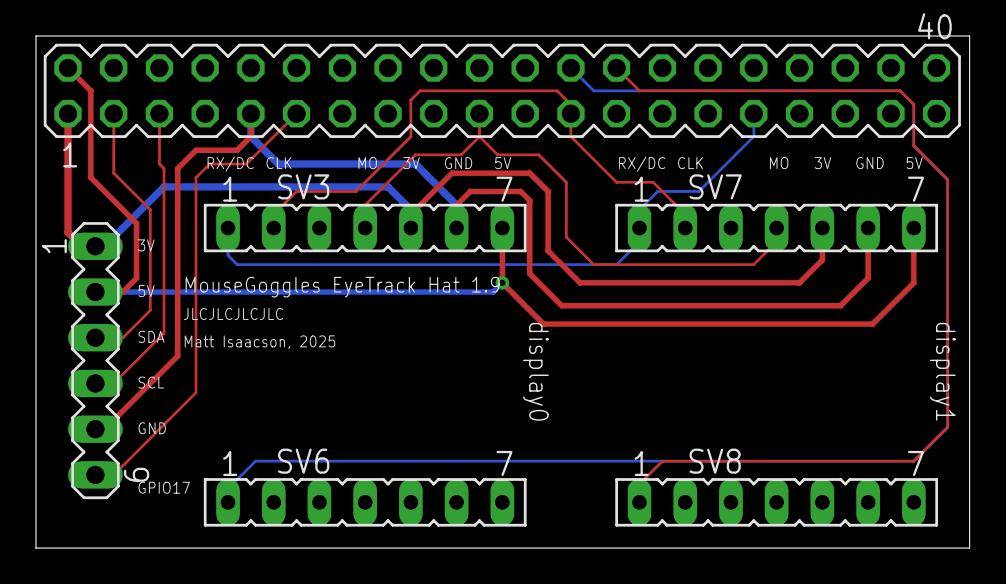
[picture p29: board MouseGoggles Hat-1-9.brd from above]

Board: 2 copper layers, 51.9 x 28.4 mm, 6 parts (0 on the bottom side), 11 nets.

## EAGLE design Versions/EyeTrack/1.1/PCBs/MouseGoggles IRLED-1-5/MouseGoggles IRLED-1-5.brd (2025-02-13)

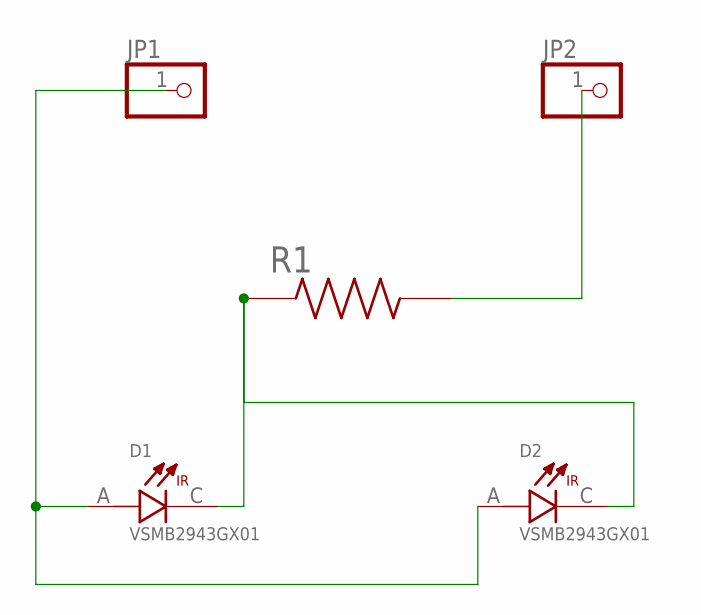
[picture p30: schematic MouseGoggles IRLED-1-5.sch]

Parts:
D1, D2: VSMB2943GX01; DIO_VSMB2943GX01
JP1, JP2: PINHD-1X1; 1X01
R1: RC0805FR-07100RL; RESC2012X60N

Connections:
unnamed: JP2.1, R1.2
unnamed: D1.A, D2.A, JP1.1
unnamed: D1.C, D2.C, R1.1

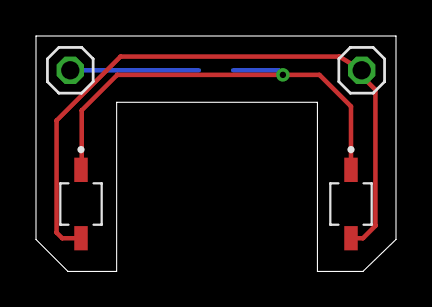
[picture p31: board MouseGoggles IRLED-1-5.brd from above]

Board: 2 copper layers, 20.0 x 13.1 mm, 5 parts (1 on the bottom side), 3 nets.

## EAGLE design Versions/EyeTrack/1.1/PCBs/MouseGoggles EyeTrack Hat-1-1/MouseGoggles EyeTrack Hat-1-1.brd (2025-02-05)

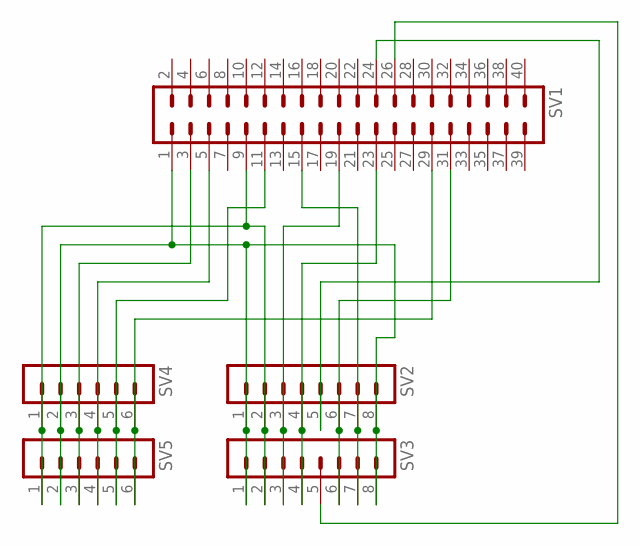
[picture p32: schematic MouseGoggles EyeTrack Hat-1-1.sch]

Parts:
SV1: MA20-2
SV2, SV3: MA08-1
SV4, SV5: MA06-1

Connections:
unnamed: SV1.1, SV2.1, SV2.8, SV3.1, SV3.8, SV4.2, SV5.2
unnamed: SV1.9, SV2.2, SV3.2, SV4.1, SV5.1
unnamed: SV1.19, SV2.3, SV3.3
unnamed: SV1.23, SV2.4, SV3.4
unnamed: SV1.24, SV2.5
unnamed: SV1.26, SV3.5
unnamed: SV1.31, SV2.6, SV3.6
unnamed: SV1.15, SV2.7, SV3.7
unnamed: SV1.3, SV4.3, SV5.3
unnamed: SV1.5, SV4.4, SV5.4
unnamed: SV1.11, SV4.5, SV5.5
unnamed: SV1.29, SV4.6, SV5.6

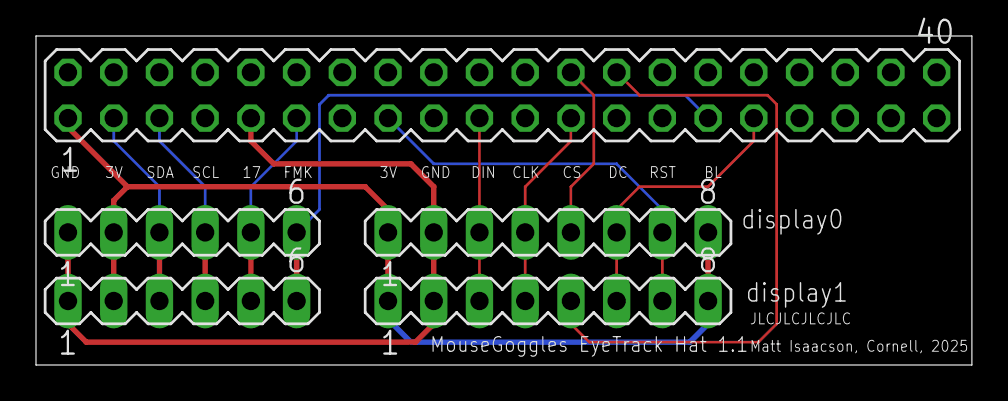
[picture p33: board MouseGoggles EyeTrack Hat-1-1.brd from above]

Board: 2 copper layers, 52.0 x 18.3 mm, 5 parts (0 on the bottom side), 12 nets.

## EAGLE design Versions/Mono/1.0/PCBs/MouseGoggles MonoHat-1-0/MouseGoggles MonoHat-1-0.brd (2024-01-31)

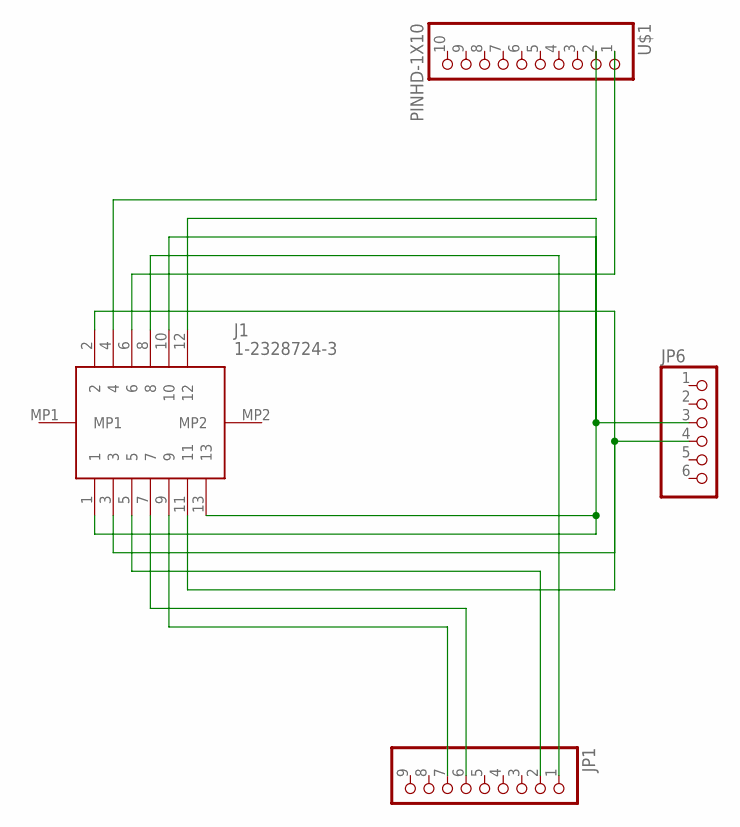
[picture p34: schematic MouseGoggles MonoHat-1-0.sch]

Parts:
J1: 1-2328724-3; 123287243
JP1: PINHD-1X9; 1X09-BIG
JP6: PINHD-1X6B; 1X06-BIG
U$1: PINHD-1X10; 1X10-BIG

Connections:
unnamed: J1.1, J1.10, J1.12, J1.13, JP6.3
unnamed: J1.2, J1.3, J1.11, JP6.4
unnamed: J1.5, JP1.2
unnamed: J1.6, U$1.1
unnamed: J1.8, JP1.1
unnamed: J1.4, U$1.2
unnamed: J1.7, JP1.6
unnamed: J1.9, JP1.7

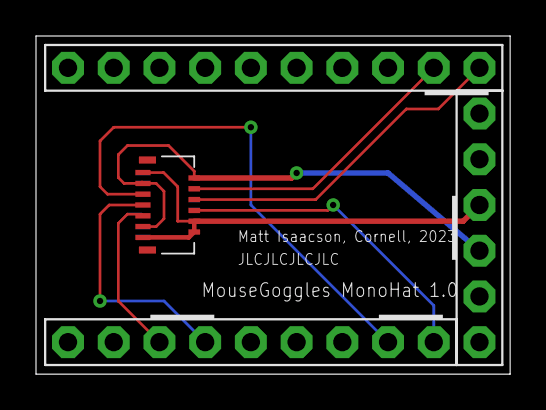
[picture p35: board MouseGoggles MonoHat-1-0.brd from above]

Board: 2 copper layers, 26.3 x 18.8 mm, 4 parts (0 on the bottom side), 8 nets.

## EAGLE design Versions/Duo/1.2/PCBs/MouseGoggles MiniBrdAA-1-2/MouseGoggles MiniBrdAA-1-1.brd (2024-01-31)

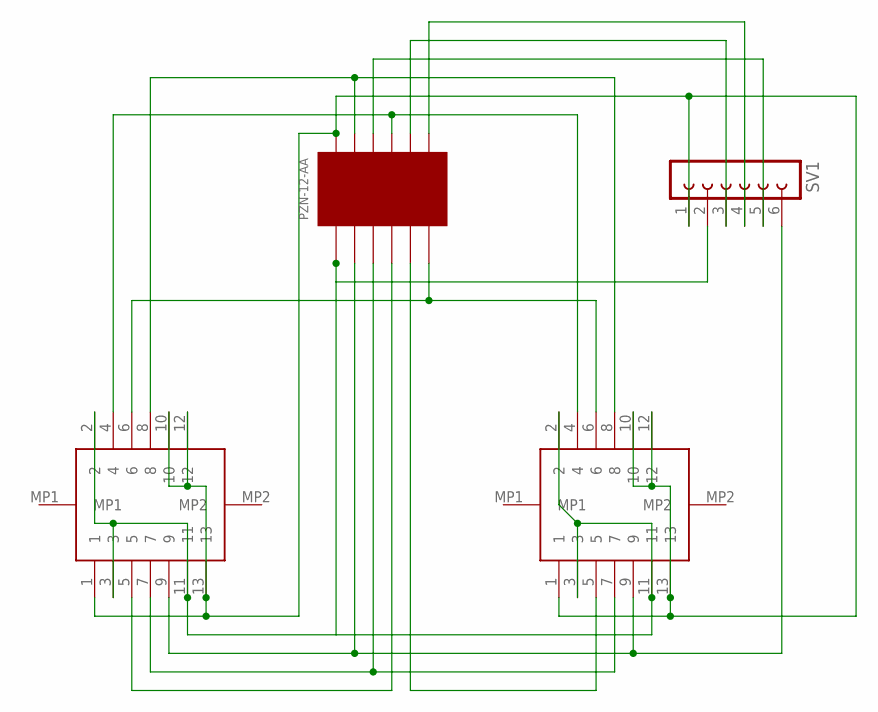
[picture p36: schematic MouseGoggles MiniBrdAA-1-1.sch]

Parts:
J1, J2: 1-2328724-3; 123287243
SV1: FE06-1; FE06
U$1: PZN_12_AA; OMN_PZN_NANO_6X2

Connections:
unnamed: J1.2, J1.3, J1.11, J2.2, J2.3, J2.11, SV1.2, U$1.P$2 (2)
unnamed: J1.1, J1.10, J1.12, J1.13, J2.1, J2.10, J2.12, J2.13, SV1.1, U$1.P$1 (1)
unnamed: J1.9, J2.9, SV1.6, U$1.P$4 (4)
unnamed: J1.7, J2.7, U$1.P$6 (6)
unnamed: J1.5, U$1.P$8 (8)
unnamed: J2.5, U$1.P$10 (10)
unnamed: J1.6, J2.6, U$1.P$12 (12)
unnamed: J1.8, J2.8, U$1.P$3 (3)
unnamed: J1.4, J2.4, U$1.P$7 (7)
unnamed: SV1.5, U$1.P$5 (5)
unnamed: SV1.3, U$1.P$9 (9)
unnamed: SV1.4, U$1.P$11 (11)

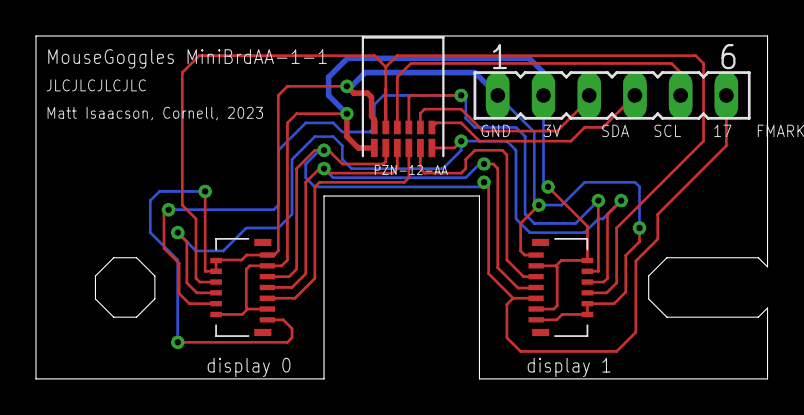
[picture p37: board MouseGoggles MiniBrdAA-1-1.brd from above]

Board: 2 copper layers, 40.6 x 19.1 mm, 4 parts (0 on the bottom side), 12 nets.

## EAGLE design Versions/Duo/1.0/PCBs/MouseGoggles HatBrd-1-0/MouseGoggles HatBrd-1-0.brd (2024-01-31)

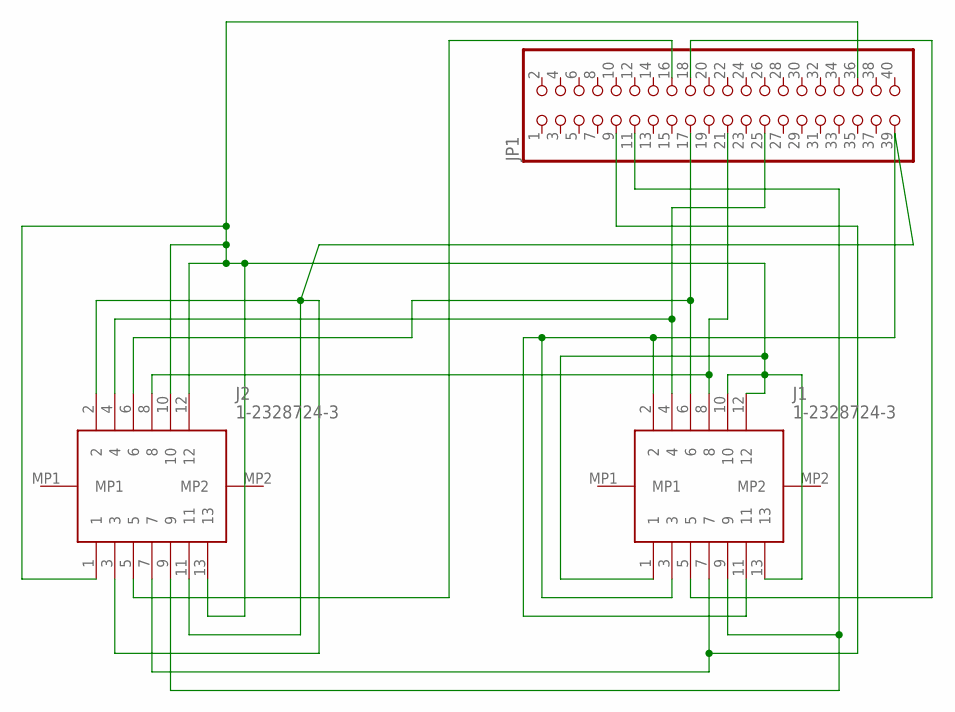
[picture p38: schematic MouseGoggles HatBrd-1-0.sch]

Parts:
J1, J2: 1-2328724-3; 123287243
JP1: PINHD-2X20-BIG; 2X20-BIG

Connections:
unnamed: J1.2, J1.3, J1.11, J2.2, J2.3, J2.11, JP1.39
unnamed: J1.8, J2.8, JP1.21
unnamed: J1.6, J2.6, JP1.17
unnamed: J1.5, JP1.18
unnamed: J1.1, J1.10, J1.12, J1.13, J2.1, J2.10, J2.12, J2.13, JP1.36
unnamed: J1.4, J2.4, JP1.25
unnamed: J1.7, J2.7, JP1.9
unnamed: J1.9, J2.9, JP1.11
unnamed: J2.5, JP1.16

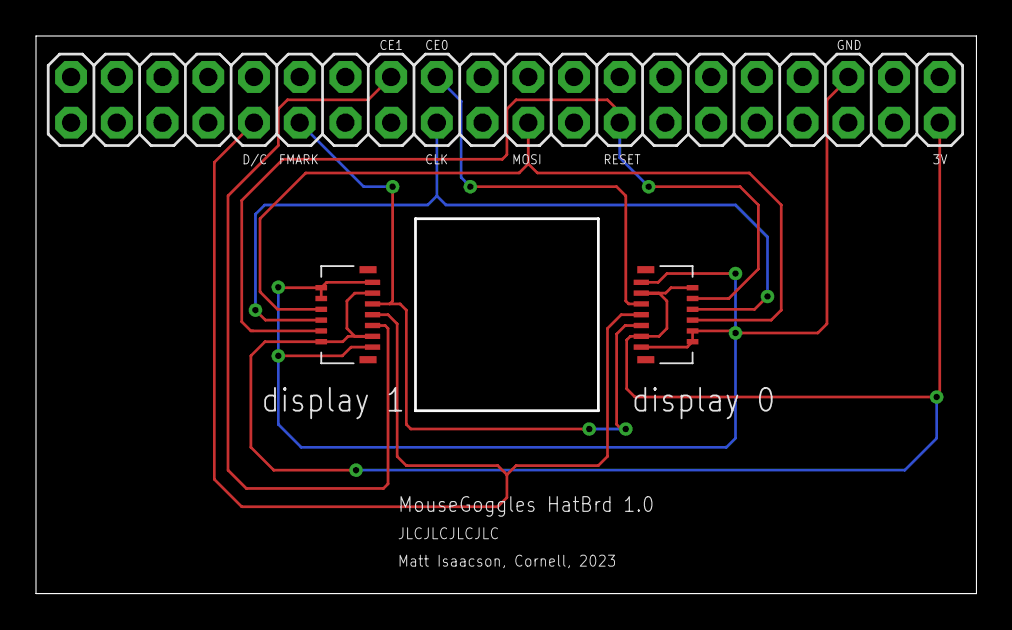
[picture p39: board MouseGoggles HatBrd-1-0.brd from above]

Board: 2 copper layers, 52.2 x 31.0 mm, 3 parts (0 on the bottom side), 9 nets.

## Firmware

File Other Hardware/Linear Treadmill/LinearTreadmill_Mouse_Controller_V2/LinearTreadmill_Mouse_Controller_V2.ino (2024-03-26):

// EncoderInterfaceT3

//  Edited by Amanda Huang, Matthew Isaacson
//  07/13/2023

//  Read the encoder and translate to a distance and send over USB-Serial and DAC
//  Teensy LC Arduino 2.1.1 with Teensy Extensions
//
//  This designed to be easy to assemble. The cables are soldered directly to Teensy 3.2.
//  Encoder A - pin 0
//  Encoder B - pin 1
//  Encoder VCC - Vin
//  Encoder ground - GND
//  Analog Out - A12/DAC
//  Analog ground - AGND
//
// Steve Sawtelle
// jET
// Janelia
// HHMI 
// 



#define VERSION "20180207"
// ===== VERSIONS ======

//library for mouse movement
#include "Mouse.h"

#define MAXSPEED    1000.0f  // maximum speed for dac out (mm/sec)
#define MAXDACVOLTS 2.5f    // DAC ouput voltage at maximum speed
#define MAXDACCNTS  4095.0f // maximum dac value
#define maxMouseval 127.0f

float maxDACval = MAXDACVOLTS * MAXDACCNTS / 3.3; // limit dac output to max allowed
float mouseGain = 1.0;

#define encAPin 0
#define encBPin 1
#define dacPin  A12
//#define idxPin  2  // not used here

// counts per rotation of treadmill encoder wheel
// 200 counts per rev
// 1.03" per rev
// so - 1.03 * 25.4 * pi / 200 /1000 = microns/cnt

#define MM_PER_COUNT 410950  // actually 1/10^6mm per count since we divide by usecs
#define DIST_PER_COUNT ((float)MM_PER_COUNT/1000000.0)
//(float)0.41095

#define SPEED_TIMEOUT 50000  // if we don't move in this many microseconds assume we are stopped

static float runSpeed = 0;
volatile uint32_t lastUsecs;
volatile uint32_t thisUsecs;
volatile uint32_t encoderUsecs;
uint32_t now;
volatile float distance = 0;
bool oldencAState=0;
bool encAState;
bool encBState;
float dacval;

int dir = 1;

int8_t forwardSpeed = 0;

void setup()
{
  //Serial.begin(192000);
  //while( !Serial);   // if no serial USB is connected, may need to comment this out
  pinMode(encAPin, INPUT_PULLUP); // sets the digital pin as input
  pinMode(encBPin, INPUT_PULLUP); // sets the digital pin as input
  analogWriteResolution(12);
  Mouse.begin();
  //Serial.print("Treadmill Interface V: ");
  //Serial.println(VERSION);
  //Serial.println("distance,speed");
  //Serial.println(maxDACval);

  lastUsecs = micros();
}

void loop() 
{ 
  now = micros();
  //treadmill is stopped 
  if( (now > lastUsecs) && ((now - lastUsecs) > SPEED_TIMEOUT)  )
  {   // now should never be < lastUsecs, but sometiems it is
      // this is from the old code, necessary?
     runSpeed = 0;
     analogWrite(dacPin, maxDACval/2);
  }    

// Polling
// there are 3 cases 
// 1. enc A is on a rising edge and encA=encB=1
// This is backwards movement on the treadmill. It will result in an 
// output voltage on pin A12 to be between 0 and ~1551.
// faster motion is closer to 0

// 2. enc A is on a rising edge and encA!=enc B
// This is forward movement on the treadmill. It will result in an 
// output voltage on pin A12 to be between ~1551 and ~ 3102

// 3. enc A is not changing, dac val is ~1551. 

//Questions: what should the delay be?
//Question: does there need to be a buffer region around speed zero for fwd and bwd motion?

//check ENCA pin and ENCB pin 
  encAState = digitalRead(encAPin);
  encBState = digitalRead(encBPin);

//check if there is motion; rising of encApin; 
  if ((oldencAState ==0) && (encAState==1))
  {
    //figure out direction; change volt output based on the dir  
    //ENCA == ENCB: bwD motion,  ENCA != ENCB FWD motion
    dir= (encAState==encBState)*-2 +1;
    thisUsecs = micros();
    encoderUsecs = thisUsecs - lastUsecs;
    lastUsecs = thisUsecs;
    runSpeed = (float)MM_PER_COUNT / encoderUsecs;
    distance += DIST_PER_COUNT;

    dacval = (maxDACval/2)+ dir*(runSpeed/MAXSPEED * (maxDACval))/2; 
    forwardSpeed =  mouseGain*dir*(runSpeed/MAXSPEED * (maxMouseval));
    if( dacval < 0 ) dacval = 0;
    if( dacval > maxDACval) dacval = maxDACval;
    // Serial.print("distance:");
    // Serial.print(distance);
    // Serial.print(",speed:");
    // Serial.println(runSpeed);    
    // Serial.print("dac: ,");
    // Serial.print(dacval); 
    // Serial.print(",dir:");
    // Serial.print(dir);
    analogWrite(dacPin,(uint16_t) dacval);
    Mouse.move(0,forwardSpeed,0);
  }
//all cases 
  oldencAState= encAState;
  delay(0.5);
}

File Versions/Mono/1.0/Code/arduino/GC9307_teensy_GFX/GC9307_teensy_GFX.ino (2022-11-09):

#include <Adafruit_GFX.h>    // Core graphics library from Adafruit, slightly modified
#include "Adafruit_GC9307.h" // Driver for GC9307-based display (modified from Adafruit_ST7789)
#include <SPI.h>             // SPI library for communication to the display
#include <EEPROM.h>          // EEPROM library (for seldom-used on-board data storage)
#include "logo_bitmap.h"     // hex bitmap of Cornell Engineering and SN-lab logos

#define TFT_CS  10 // chip-select pin
#define TFT_RST 14 // reset pin
#define TFT_DC  6 // data/command pin
#define TRIG_OUT 0 // start-trigger output pin
#define TRIG_IN 1 //start-trigger input 

//initialize program basics
int width = 240; // width of display in pixels
int height = 210; // height of display in pixels
float pi = 3.14159;
int demoEPPA = 0; // eeprom address for stored demo byte
byte demo; // 111=run demo, 110=don't run demo
int backgroundEPPA[3] = {1, 2, 3}; //eeprom address for background color RGB values;
byte backgroundRGB[3]; //[red, green, blue] color values of display background

//initialize default pattern parameters
uint8_t commandID = 0;
uint8_t centerPosition[2] = {128, 128}; //[x, y] center coordinate of pattern relative to display center
uint8_t numGratings = 2; //number of repeated dark/bright bars in grating
uint8_t barWidth = 40; //width of each dark/bright bar (in pixels) of grating
uint8_t colorBytes[3][3] = {{0, 0, 30},{0, 0, 0},{0, 0, 15}};
uint8_t angleBytes[2] = {0, 0}; //angle of pattern, separated into halves for 0-360 deg (1 byte only allows 0-255)
uint8_t temporalFrequencyDHz = 10; //speed of gratings/flickers (in deci-Hertz)
uint8_t patternType = 1; //1=square-wave grating, 2=sine-wave grating, 3=flicker
uint8_t preDelayDs = 0; //delay (in s) to wait after start command until pattern is drawn
uint8_t durationDs = 1; //duration (in deci-seconds) to draw pattern
uint8_t wait4Trigger = 0; //whether to wait for TRIG_IN signal to start pattern
float benchmarkHz; //maximum temporal frequency a pattern can be displayed (calculated later)
unsigned long numPatternsDisplayed = 0;
unsigned long startTime = 0;

//initialize other common variables
uint8_t readDelay = 100; //duration (in ms) between checking for new incoming serial data
int i, r, c, e, startCommand = 0;
byte * bytes4x;
unsigned long startMs, endMs, startUs, endUs;
float durUs;
uint16_t backgroundColor, prevBackgroundColor;
float versionID = 9307.1;

//create prototypes for every function in this program (I still don't know why this is necessary...)
void runDemo();
void wait4Serial(uint8_t wait, int num2wait4);
uint8_t readSerialMessage();
void serialWriteLong(unsigned long UL);
void serialWriteFloat(float F);
float deg2rad(uint16_t deg);
void drawPattern(uint8_t type, uint8_t pos[2], uint8_t numrepeats, uint8_t barW, 
        uint8_t aBytes[2], uint8_t freq, uint8_t color[3][3], uint8_t pre, 
        uint8_t dur, int wait4Trig, unsigned long &startT, float &bmark);
        
//instantiate display with driver for GC9307-based display
Adafruit_GC9307 tft = Adafruit_GC9307(TFT_CS, TFT_DC, TFT_RST);

void setup(void) {
  Serial.begin(9600); //on the Teensy, this doesn't set the speed -- it's 12 Mbit/sec no matter what
  Serial.println(F("GC9307 Display Test"));
  tft.init(width, height); //initialize the display
  tft.setSPISpeed(96000000); //set this to be as fast as the display can handle
  Serial.println(F("Initialized"));
  
  //check EEPROM storage for demo byte, write 1 to it if it hasn't been set yet
  demo = EEPROM.read(demoEPPA);
  if (demo!=110 && demo!=111) { //if demo byte hasn't bee stored yet?
    demo = 111;
    EEPROM.write(demoEPPA, demo);
    delay(10);
  }

  //check EEPROM for stored backgroundColor 
  for (i=0;i<3;i++) {
    backgroundRGB[i] = EEPROM.read(backgroundEPPA[i]);
  }
  backgroundColor = backgroundRGB[2]; //add blue value to lowest 5 bits
  backgroundColor = backgroundColor<<6; //shift blue over by 6 bits, leaving lower 6 bits empty now
  backgroundColor |= backgroundRGB[1]; //add green value to lowest 6 bits
  backgroundColor = backgroundColor<<5; //shift blue/green over by 5 bits, leaving lowest 5 empty
  backgroundColor |= backgroundRGB[0]; //add red value to lowest 5 bits
  prevBackgroundColor = backgroundColor;
  tft.fillScreen(backgroundColor);

  pinMode(TRIG_IN, INPUT);
  pinMode(TRIG_OUT, OUTPUT);
  digitalWrite(TRIG_OUT, LOW);
}

void loop() { //main program loop
  if (demo==111) {runDemo();} //self-explanatory, right?

  //wait for incoming instructions over serial connection
  wait4Serial(readDelay, 1); //wait for (at least) 1 available byte
  
  //read incoming command and data over serial
  commandID = readSerialMessage(); //read incoming message ID byte (specifies what data is coming next)
  switch (commandID) {
    case 0: //command to send version ID back over serial
      serialWriteFloat(versionID);
      break;
      
    case 101: //command to set parameters (and possibly start displaying the pattern)
      wait4Serial(readDelay, 21); //wait for 21 available bytes

      startCommand = readSerialMessage(); //byte 1
      patternType = readSerialMessage(); //byte 2
      for (r=0;r<3;r++) {
        for (c=0;c<3;c++) {
          colorBytes[r][c] = readSerialMessage(); //bytes 3-11
        }
      }
      barWidth = readSerialMessage(); //byte 12
      numGratings = readSerialMessage(); //byte 13
      angleBytes[0] = readSerialMessage(); //byte 14
      angleBytes[1] = readSerialMessage(); //byte 15
      temporalFrequencyDHz = readSerialMessage(); //byte 16
      centerPosition[0] = readSerialMessage(); //byte 17
      centerPosition[1] = readSerialMessage(); //byte 18
      preDelayDs = readSerialMessage(); //byte 19
      durationDs = readSerialMessage(); //byte 20
      wait4Trigger = readSerialMessage(); //byte 21
      
      //fill screen with background color, if changed
      backgroundColor = colorBytes[2][2]; //add blue value to lowest 5 bits
      backgroundColor = backgroundColor<<6; //shift blue over by 6 bits, leaving lower 6 bits empty now
      backgroundColor |= colorBytes[2][1]; //add green value to lowest 6 bits
      backgroundColor = backgroundColor<<5; //shift blue/green over by 5 bits, leaving lowest 5 empty
      backgroundColor |= colorBytes[2][0]; //add red value to lowest 5 bits
      if (backgroundColor!=prevBackgroundColor) {
        //write new background color to EEPROM
        for (i=0;i<3;i++) {
          EEPROM.write(backgroundEPPA[i],colorBytes[2][i]);
        }
        //fill screen with new background color
        tft.fillScreen(backgroundColor);
        prevBackgroundColor = backgroundColor;
      }
      break;

    case 110: //set demo mode off
      demo = commandID;
      if (demo!=EEPROM.read(demoEPPA)) {
        EEPROM.write(demoEPPA, demo);
        delay(10);
      }
      //send message confirming that demo mode is off
      Serial.write(112);
      Serial.write(212);
      break;
      
    case 111: //set demo mode on
      demo = commandID;
      if (demo!=EEPROM.read(demoEPPA)) {
        EEPROM.write(demoEPPA, demo);
        delay(10);
      }
      break;

    case 121: //send teensy timestamps (for PC/Teensy clock synchronization)
      startTime = millis(); 
      serialWriteLong(startTime); //send time in ms from teensy program start
      break;

    case 131: //reset background
      tft.fillScreen(backgroundColor);
      break;
      
    default: //give error message if command ID not recognized
      Serial.write(225); //ID that command was not recognized
      Serial.write(commandID);
      break;
  }
  
  //display pattern (if start command was received)
  if (startCommand==1) {
    //display pattern
    startTime = millis();
    drawPattern(patternType, centerPosition, numGratings, barWidth, angleBytes, temporalFrequencyDHz, colorBytes, preDelayDs, durationDs, wait4Trigger, startTime, benchmarkHz);
    
    //send data about previously displayed pattern back over serial
    numPatternsDisplayed++;
    Serial.write(201); //byte 1: host-side command ID for incoming data
    serialWriteLong(numPatternsDisplayed); //bytes 2-5: number of patterns displayed so far
    serialWriteLong(startTime); //bytes 6-9: pattern start timestamp
    Serial.write(patternType); //byte 10
    for (r=0;r<3;r++) {
      for (c=0;c<3;c++) {
        Serial.write(colorBytes[r][c]); //bytes 11-19
      }
    }
    Serial.write(barWidth); //byte 20
    Serial.write(numGratings); //byte 21
    Serial.write(angleBytes,2); //bytes 22-23
    Serial.write(temporalFrequencyDHz); //byte 24
    Serial.write(centerPosition,2); //bytes 25-26
    Serial.write(durationDs); //byte 27
    Serial.write(preDelayDs); //byte 28
    Serial.write(wait4Trigger); //byte 29
    serialWriteFloat(benchmarkHz); //bytes 30-33

    startCommand = 0; //reset startCommand to 0 to wait for next pattern
  }
}


//wait for desired amount of available serial data bytes
void wait4Serial(uint8_t wait, int num2wait4) {
  int bytesavail = Serial.available();
  while (bytesavail<num2wait4) {
    delay(wait);
    bytesavail = Serial.available();
  }
}


//read serial message
uint8_t readSerialMessage() {
  int msg16 = Serial.read();
  uint8_t msg = 0;
  if (msg16!=-1) {
    msg = msg16;
  }
  return msg;
}

void serialWriteLong(unsigned long UL) {
  bytes4x = (byte *) &UL;
  Serial.write(bytes4x,4); //send 1 unsigned long as 4 bytes
}

void serialWriteFloat(float F) {
  bytes4x = (byte *) &F;
  Serial.write(bytes4x,4); //send 1 float as 4 bytes
}

float deg2rad(uint16_t deg) {
  return (deg*pi/180); //convert degrees to radians
}
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

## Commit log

2022-11-02 Added working files from test Raspberry Pi
2022-11-09 Added hardware files
    [MouseEyepieceBack_V3.stl, MouseEyepieceFront_V3.stl, RaspberryPiCaseBack_V3.stl, RaspberryPiCaseFront_V3.stl]
2022-11-09 rearrange hardware files; update readme
    [Parts Lists.xlsx]
2022-11-10 Add 3D prints
    [MouseEyepieceBack_V3.stl, MouseEyepieceFront_V3.stl, RaspberryPiCaseBack_V3.stl, RaspberryPiCaseFront_V3.stl]
2022-11-12 Added zipped PCB files
2022-12-15 Updated 3D print files, monocular display software instructions
    [DisplayHolder_V1.stl, LensHolder_V1.stl, Parts Lists.xlsx, RaspberryPiCaseBack_V3.stl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]
2023-06-13 Added headset assembly text instructions
2023-06-13 Fixed innacuracy in gdshader; Added Pi header to parts list
    [Parts Lists.xlsx]
2023-06-26 Added test assembly files
    [Bill of Materials for RaspyGC9307_V1.csv, Pick Place for RaspyGC9307_V1.csv]
2023-06-26 Update Bill of Materials for RaspyGC9307_V1.csv
    [Bill of Materials for RaspyGC9307_V1.csv]
2023-09-01 Add published data/metadata
    [Parts Lists.xlsx, Reaction Log-Amanda Huang.xlsx, Reaction Log-Annabella Wulf.xlsx, Reaction Log-Combined.xlsx]
2023-09-02 Added files for small form factor headset
    [Parts Lists.xlsx, miniHeadet_V1.stl]
2023-10-28 Added assembly photos
2023-10-30 Update README.md
    Not yet validated for newest Raspberry Pi OS (bookworm), tested OS version (bullseye) is now legacy.
2023-11-10 Updated files for small form factor headset
    [miniHeadset_V1.stl, miniHeadset_V2_backing.stl, miniHeadset_V2_eyepiece.stl]
2023-11-10 Updated small form factor headset 3D prints
    [Parts Lists.xlsx]
2023-11-29 Lowered default SPI rate and frame rate
2024-01-14 Added files for MouseGoggles version 1.5
    [MouseGoggles 1.5 EyepieceBackV2.step, MouseGoggles 1.5 EyepieceBackV2.stl, MouseGoggles 1.5 EyepieceEnclosureBackV2.step, MouseGoggles 1.5 EyepieceEnclosureBac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]
2024-01-14 Update Parts, Assembly, and Installation README.md
2024-01-31 Updated versions
    -Added new MouseGoggles versions: 1.0-1.5
    -Added design files (3D .step, PCB schematic, layout, eagle projects) for all versions
    -Restructured assembly/installation instructions to be version-specific
    -Added "Other Hardware", including linear treadmill and headbars/mounts
    -Removed outdated Godot projects
    -
    [Bill of Materials for MouseGoggles HatBrd-1-0.csv, Bill of Materials for RaspyGC9307_V1.csv, MouseEyepieceBack_V3.stl, MouseEyepieceFront_V3.stl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]
2024-03-26 Added EyeTracking! Reformatted versions for Mono/Duo/EyeTrack models
    [Bill of Materials for MouseGoggles HatBrd-1-0.csv, EyeTrack 1.0 EyepieceEnclosureV6.step, EyeTrack 1.0 EyepieceEnclosureV6.stl, EyeTrack 1.0 MountV6.step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]
2025-02-05 Added files for EyeTrack 1,1
    [Camera Clip V1.step, Camera Clip V1.stl, Enclosure Back V3.step, Enclosure Back V3.stl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]
2025-02-13 Update IRLED board
    [MouseGoggles IRLED-1-5.brd]
2025-02-21 Add assembly images
2025-07-04 Updated instructions on camera availability
2025-10-01 Added initial files for Duo V1.9 and EyeTrack V1.9
    [BracketA 2.0 V1.step, BracketA 2.0 V1.stl, BracketB 2.0 V1.step, BracketB 2.0 V1.stl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]
2026-01-23 Added initial design files for EyeTrack 2.0
    [Bracket50 V1.step, Bracket50 V1.stl, Bracket55 V1.step, Bracket55 V1.stl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]
2026-01-28 Added config for dual cameras
2026-02-02 Updated LensClip, Bracket, and Assembly instructions
    [Bracket50 V1.step, Bracket50 V1.stl, Bracket55 V1.step, Bracket55 V1.stl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]
2026-02-02 Fix file paths in README for installation instructions
    Updated file paths in installation instructions for Raspberry Pi.
2026-02-02 Fix Display 2 pin assignments and update instructions
    Corrected pin assignments for Display 2 and improved clarity in installation instructions.
2026-02-03 Revise assembly and wiring instructions in README
    Updated images and instructions for assembling and wiring MouseGoggles EyeTrack 2.0.
2026-02-03 Added assembly images
2026-02-09 Revise camera installation instructions
    Updated wiring instructions for displays and cameras, and clarified steps to start the camera controller and Godot game engine.
2026-02-09 Set common defaults
    default: 50-deg bracket; horizontal headset position (not pitched up or down); eye-tracking recording enabled
2026-02-10 Revise EyeTrack 2.0 assembly notes for clarity
    Updated the description of the EyeTrack 2.0 assembly process to clarify the current state of eye imaging quality and the need for external IR illumination.
2026-02-22 Added new IR pupil imaging design
    - Added new 3D designs to support IR LEDs
    - Updated Godot project to remove red eye illumination
    - Updated instructions to reflect these changes
    [CameraClip V1.step, CameraClip V1.stl, CameraClip V2.step, CameraClip V2.stl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]
2026-06-08 Improved camera setting controls
2026-06-08 Added new IR-sensitive camera; improved camera scripts; instructions for calibrating cameras
